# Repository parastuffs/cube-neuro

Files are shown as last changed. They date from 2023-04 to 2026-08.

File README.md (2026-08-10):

# Early Curiosity - Cube

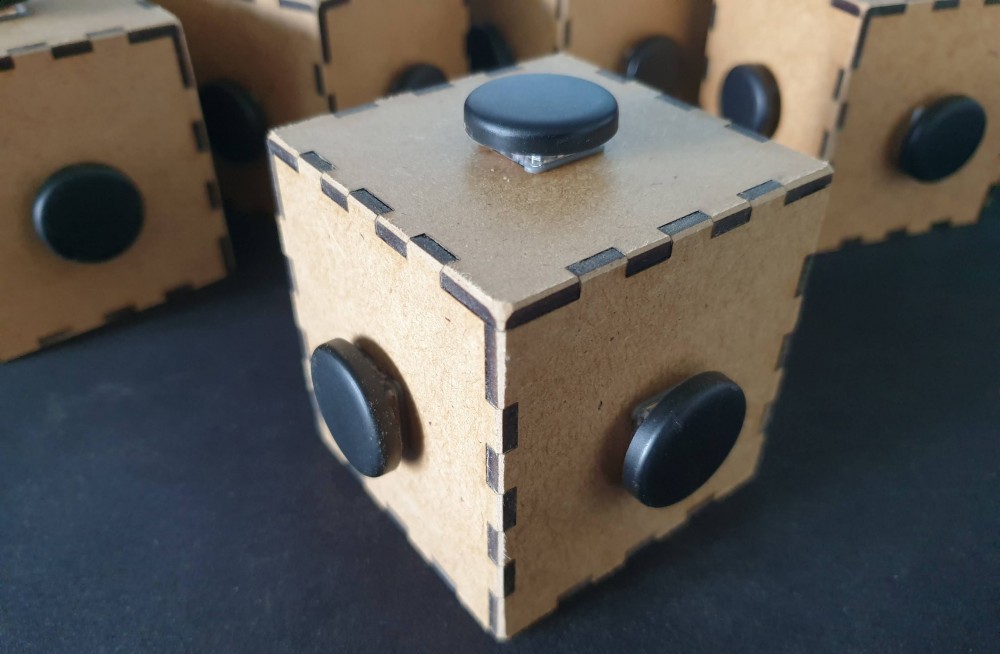
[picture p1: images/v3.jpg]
Cubes


This is the documentation for the **third version** of the cube. v1 is available [here](https://github.com/parastuffs/cube-neuro/blob/main/README_V1.md) and v2 [here](https://github.com/parastuffs/cube-neuro/blob/main/README_V2.md).
Pictures of the development are available [online](https://photos.app.goo.gl/61a8nF2CPd1NJpt47)(v2 [here](https://photos.app.goo.gl/r4oXzCXrc1rNYwXG9)).

The cube has a button on five of its faces, and a hatch on the bottom face.
Under the hatch, there is:
- A USB-C port for programming and battery charging. 
> [!IMPORTANT]  
> To charge the battery, the cube needs to be **on**.
- A switch to turn the cube on and off.
- A micro-SD reader.

In the demonstration mode, pressing a button might trigger a sound depending on the cube configuration.
> [!IMPORTANT]
> To switch to experiment mode, you need to keep any of the buttons pressed for two seconds.
In order to come back to demonstration mode, you need to reboot the cube by turning it off and on again.

In experiment mode, pressing a button never triggers a sound, but all events are saved to the SD card in a `.csv` file. It follows this structure:

| observation | face | pression_start | pression_stop | sound | isExperiment |
| --- | --- | --- | --- | --- | --- |
| Observation count, incremental | 1 to 5 value of the pressed button | Time of start of press | Time of end of press | Sound played (1) or not (0) | Press durring demo (0) or experiment (1) |

Time measurement is in milliseconds, 0 being the powering up of the cube.

### Change the sound played during demonstration mode
The sound must be located at the root of the micro-SD card and **must** be named `sound.mp3`.

### The cube and dates
The micro-controller does not have any notion of the actual date. With each reboot, it starts couting time from zero again. All files are thus created with an erroneous creation date which should be ignored.

### File structure
Upon starting for the first time, the micro-controller checks if the file `exp_id.txt` exists and does create it if it's not found.
This file contains a list of all incremental IDs of previously saved experiments.
When the cube switches to experiment mode, the micro-controller checks the last ID in that file, increment it, and create a new experiment ID.
This number `<id>` is then used to create a file `exp_<id>.csv`.

Just like audio file, experiment file names are not case sensitive (`EXP_20.csv` is the same as `exp_20.csv`) and cannot exceed eight characters without the file extension (`exp_20.csv` is valid, `experience_20.csv` or `exp_12345.csv` are not).

### Update the cube configuration
In their default configuration, the cube behave as such in demonstration mode:
- Alpha: Always play sound
- Beta: No sound
- Gamma: Sound / No sound
- Delta: No sound x7 / Sound

A more detailed guide is available [here](https://github.com/parastuffs/cube-neuro/tree/main/code) on updating the code.

### Hardware
This [file](https://github.com/parastuffs/cube-neuro/blob/main/BOM.md) has a full bill of materials. Since v3, the cube is laser cutted instead of 3D printed.

### Improvement considered
- Add an RTC to keep track of time.
- Having a configuration file for the cube type.

Copyright © 2026 Quentin Delhaye, Romain di Stasi, Claire Kabdebon, Adélaïde de Heering.

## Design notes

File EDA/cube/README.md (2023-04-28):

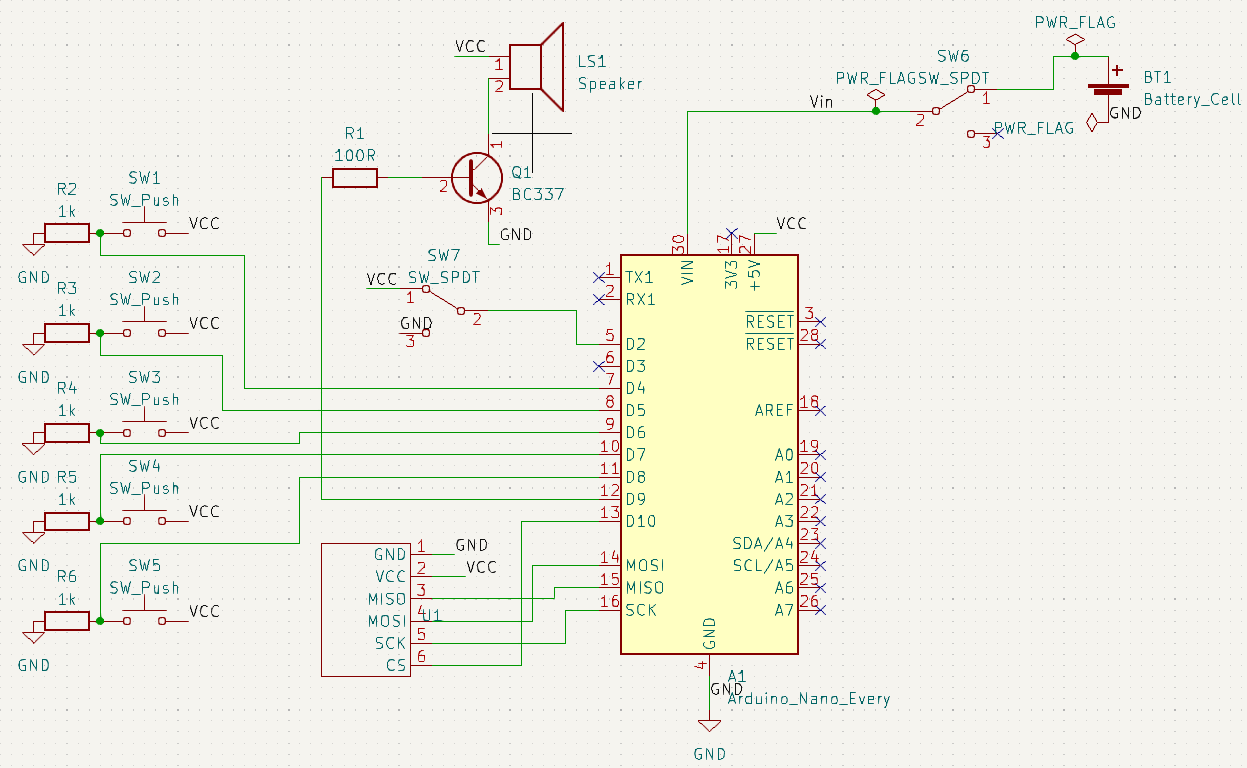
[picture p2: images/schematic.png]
Schematic


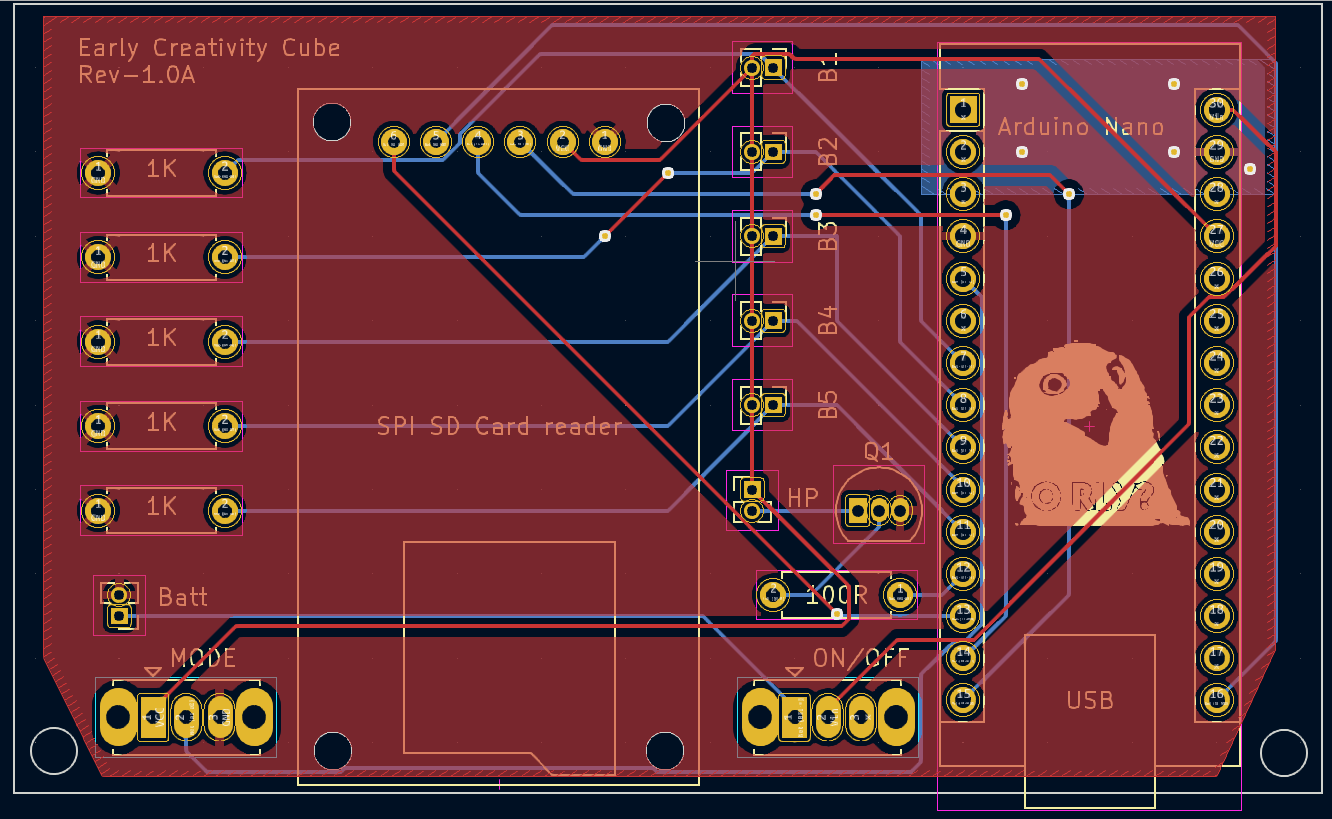
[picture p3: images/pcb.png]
PCB


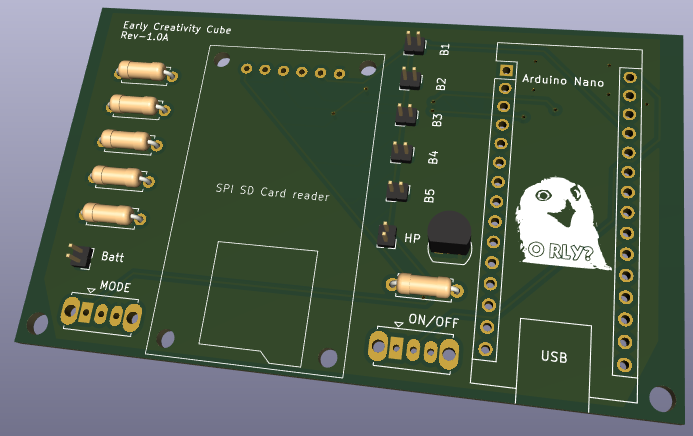
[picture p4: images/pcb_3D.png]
PCB 3D view


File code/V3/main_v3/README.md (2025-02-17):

Étant donné qu'il s'agit du même matériel, la procédure de mise à jour et de monitoring du cube est [la même que pour la V2](https://github.com/parastuffs/cube-neuro/blob/main/code/V2/README.md).

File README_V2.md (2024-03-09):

# Early Creativity - Cube

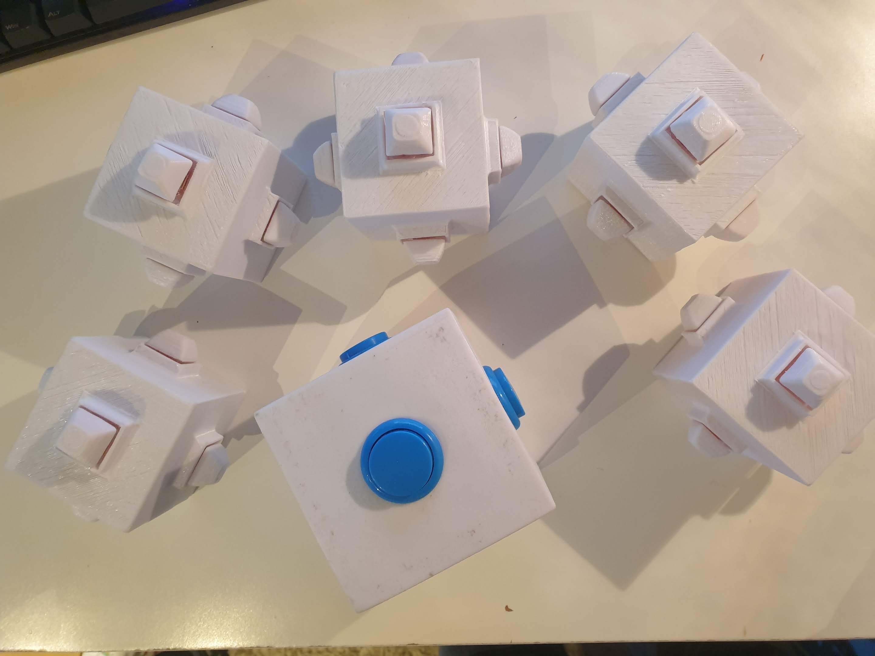
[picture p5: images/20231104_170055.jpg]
Cubes


Ceci est la documentation pour la seconde version du cube. La première version (V1) est disponible [ici](https://github.com/parastuffs/cube-neuro/blob/main/README_V1.md)
D'autres photos du développement du cube sont disponibles [en ligne](https://photos.app.goo.gl/r4oXzCXrc1rNYwXG9).

Le cube présente un bouton sur cinq de ses faces et une trappe sous sa face inférieure.
Sous la trappe se trouvent :
- Un port micro-USB pour reprogrammer le micro-contrôleur et recharger la batterie. **Attention, pour recharger la batterie, il faut connecter le câble USB et allumer le cube.**
- Un interrupteur permettant d'allumer (ON) ou éteindre (OFF) le cube.
- Un lecteur de carte micro-SD.

En mode démonstration, appuyer sur un bouton peut générer un son à l'aide du haut-parleur exposé sur la face inférieure.
**Pour passer au mode expérience, il faut maintenir un bouton enfoncé au moins deux secondes.**
Pour revenir au mode démonstration, il faut redémarrer le cube.

En mode expérience, appuyer sur un bouton ne génère aucun son, mais les pressions sont enregistrée sur la carte micro-SD dans un fichier `.csv`. Ce fichier suit la structure suivante :

| observation | face | pression_start | pression_stop | sound | isExperiment |
| --- | --- | --- | --- | --- | --- |
| Numéro de l'observation, incrémental | Valeur entre 1 et 5 du bouton appuyé | Instant de début de pression | Instant de fin de pression | Son joué (1) ou non (0) | Pression durant la démo (0) ou l'expérience (1) |

La mesure du temps se fait en milliseconde, l'instant initial étant l'allumage du cube.

Les boutons sont numérotés comme suit :
1. Face supérieure
2. Face latérale côté haut-parleur
3. Face latérale côté circuit imprimé (opposée au haut-parleur)
4. Face latérale gauche (face inférieure vers soi)
5. Face latérale droite (face inférieure vers soi)

### Changer le son joué en mode démonstration
Le son joué doit se trouver à la racine de la carte micro-SD et **doit** se nommer `sound.mp3`.

### Le cube et la notion de temps
Le micro-contrôleur n'a pas de notion de date. À chaque démarrage, il recommence à compte le temps qui passe à partir de zéro. Les fichiers créés ont donc tous la même date de création erronée qui ne doit pas être prise en compte.

### Structure des fichiers
Lors de son premier démarrage, le micro-contrôleur vérifie si le fichier `exp_id.txt` existe et le crée s'il n'est pas présent sur la carte micro-SD.
Ce dernier contient une liste des identifiants incrémentaux d'expériences enregistrées.
Au passage du cube en mode expérience (mode B), le micro-contrôleur regarde le dernier identifiant dans ce fichier et incrémente sa valeur afin de créer un nouvel identifiant d'expérience.
Cet identifiant `<id>` est ensuite utilisé pour créer un fichier `exp_<id>.csv`.

Tout comme les fichiers audio, les noms des fichiers d'expérience ne sont pas sensible à la casse (`EXP_20.CSV` est identique à `exp_20.csv`) et ne peuvent pas dépasser huit caractères, extension non-comprise (`exp_20.csv` est valable, mais `experience_20.csv` ou `exp_12345.csv` ne sont pas valable).

### Mettre à jour la configuration des cubes
Dans leur configuration par défaut, les cubes se comportent comme suit en mode démonstration :
- Alpha : son à chaque pression
- Beta : aucun son
- Gamma : son une pression sur deux
- 
- Les boutons rouges suivent le schéma suivant lors de pressions successives : pas de son / son / pas de son *ou* son / pas de son / son en fonction de la configuration souhaitée.
- Les boutons verts ne génère aucun sons.

Un guide plus détaillé est disponible [ici](https://github.com/parastuffs/cube-neuro/tree/main/code) sur la mise à jour du code sur le micro-contrôleur.

### Matériel utilisé
Le fichier [suivant](https://github.com/parastuffs/cube-neuro/blob/main/BOM.md) contient un tableau avec l'ensemble du matériel utilisé pour réaliser un cube complet.

### Améliorations possibles
- Ajouter une RTC pour que le cube connaisse la date des expériences.
- Prévoir un meilleur circuit d'amplification pour le haut-parleur afin d'obtenir un meilleur volume sonore.
- Choisir le mode de fonctionnement du cube en mode démonstration (A) via un fichier de configuration sur la carte SD.

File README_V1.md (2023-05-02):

# Early Creativity - Cube

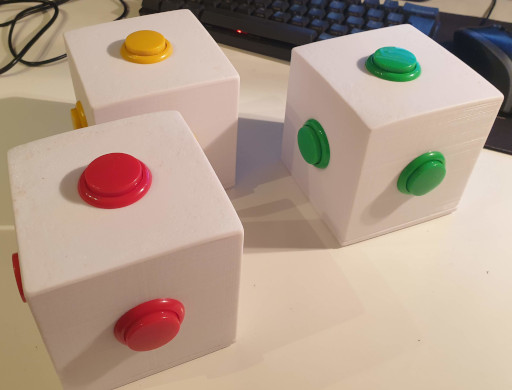
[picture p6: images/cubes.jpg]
Cubes


Le cube présente un bouton sur cinq de ses faces et une trappe sous sa face inférieure.
Sous la trappe se trouvent :
- Un port mini-USB pour reprogrammer le micro-contrôleur.
- Un port micro-USB pour recharger la batterie.
- Un interrupteur permettant d'allumer (ON) ou éteindre (OFF) le cube.
- Un interrupteur permettant de choisir le mode de fonctionnement: démonstration (A) ou expérience (B).
- Un lecteur de carte micro-SD.

En mode démonstration (A), appuyer sur un bouton peut générer un son à l'aide du haut-parleur exposé sur la face inférieure.

En mode expérience (B), appuyer sur un bouton ne génère aucun son, mais les pressions sont enregistrée sur la carte micro-SD dans un fichier `.csv`. Ce fichier suit la structure suivante :

| observation | face | pression_start | pression_stop | sound |
| --- | --- | --- | --- | --- |
| Numéro de l'observation, incrémental | Valeur entre 1 et 5 du bouton appuyé | Instant de début de pression | Instant de fin de pression | Son joué (1) ou non (0) |

La mesure du temps se fait en milliseconde, l'instant initial étant l'allumage du cube.

Les boutons sont numérotés comme suit :
1. Face supérieure
2. Face latérale côté haut-parleur
3. Face latérale côté circuit imprimé (opposée au haut-parleur)
4. Face latérale gauche (face inférieure vers soi)
5. Face latérale droite (face inférieure vers soi)

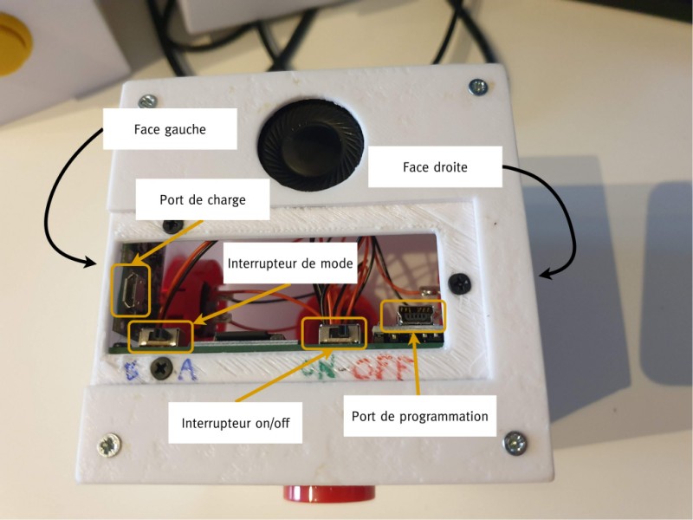
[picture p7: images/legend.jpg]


### Changer le son joué en mode démonstration
Le son joué doit se trouver à la racine de la carte micro-SD et **doit** se nommer `sound.wav`.
Le nom du fichier ne peut pas dépasser **8** caractères (hors extension). Par exemple, `maman.wav` est valable (« maman » faisant moins de huit caractères), mais `hydravion.wav` n'est pas valable.
Le système est insensible à la casse, `maman.wav` et `MaMaN.wav` sont interprétés comme étant le même fichier.

Le fichier audio **doit** respecter les contraintes suivantes :
- Codec WAV PCM 8-bit
- Mono
- Taux d'échantillonnage entre 8 kHz et 32 kHz.

La [documentation de la bibliothèque](https://github.com/TMRh20/TMRpcm/wiki) donne des informations supplémentaires si nécessaire.

### Le cube et la notion de temps
Le micro-contrôleur n'a pas de notion de date. À chaque démarrage, il recommence à compte le temps qui passe à partir de zéro. Les fichiers créés ont donc tous la même date de création erronée qui ne doit pas être prise en compte.

### Structure des fichiers
Lors de son premier démarrage, le micro-contrôleur vérifie si le fichier `exp_id.txt` existe et le crée s'il n'est pas présent sur la carte micro-SD.
Ce dernier contient une liste des identifiants incrémentaux d'expériences enregistrées.
Au passage du cube en mode expérience (mode B), le micro-contrôleur regarde le dernier identifiant dans ce fichier et incrémente sa valeur afin de créer un nouvel identifiant d'expérience.
Cet identifiant `<id>` est ensuite utilisé pour créer un fichier `exp_<id>.csv`.

Tout comme les fichiers audio, les noms des fichiers d'expérience ne sont pas sensible à la casse (`EXP_20.CSV` est identique à `exp_20.csv`) et ne peuvent pas dépasser huit caractères, extension non-comprise (`exp_20.csv` est valable, mais `experience_20.csv` ou `exp_12345.csv` ne sont pas valable).

### Mettre à jour la configuration des cubes
Dans leur configuration par défaut, les cubes se comportent comme suit en mode démonstration :
- Les boutons jaunes génèrent systématiquement un son.
- Les boutons rouges suivent le schéma suivant lors de pressions successives : pas de son / son / pas de son *ou* son / pas de son / son en fonction de la configuration souhaitée.
- Les boutons verts ne génère aucun sons.

Un guide plus détaillé est disponible [ici](https://github.com/parastuffs/cube-neuro/tree/main/code) sur la mise à jour du code sur le micro-contrôleur.

### Matériel utilisé
Le fichier [suivant](https://github.com/parastuffs/cube-neuro/blob/main/BOM.md) contient un tableau avec l'ensemble du matériel utilisé pour réaliser un cube complet.

### Améliorations possibles
- Ajouter une RTC pour que le cube connaisse la date des expériences.
- Décaler le support du circuit imprimé pour permettre à la trappe de se placer correctement sous le cube.
- Prévoir un meilleur circuit d'amplification pour le haut-parleur afin d'obtenir un meilleur volume sonore.
- Choisir le mode de fonctionnement du cube en mode démonstration (A) via un fichier de configuration sur la carte SD.

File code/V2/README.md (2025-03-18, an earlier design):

## Comment mettre le code à jour sur le micro-contrôleur ?
Le micro-contrôleur utilisé est un **Wemos Lolin32 Lite**. La méthode la plus facile pour le programmer est d'utiliser l'environnement de développement intégré (IDE) Arduino.
Ce dernier est téléchargeable [sur le site du fabricant](https://support.arduino.cc/hc/en-us/articles/360019833020-Download-and-install-Arduino-IDE).

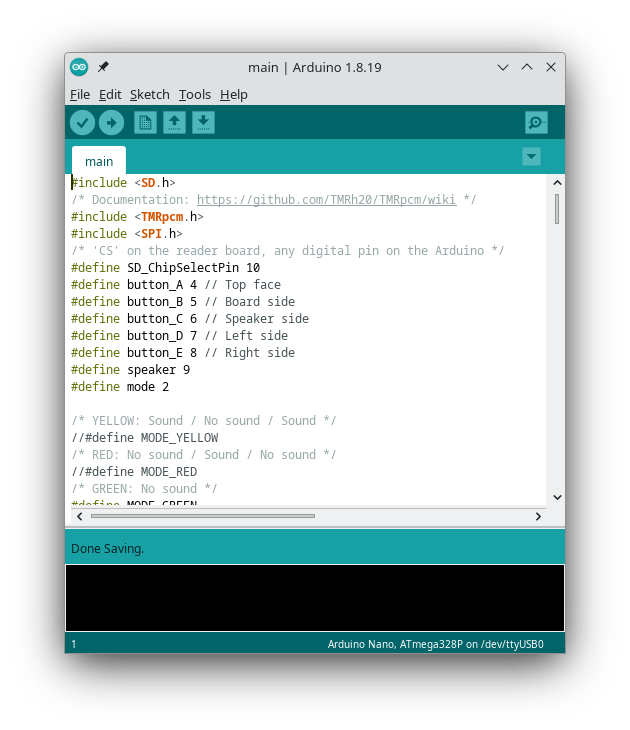
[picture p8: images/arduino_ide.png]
Arduino IDE


Avant tout, assurez-vous que les bibliothèques nécessaires sont correctement installées.

1. Allez dans le menu `Tools > Boards > Boards Manager...` et vérifiez que `ESP32` version `2.0.17` est installé.
Boards manager
2. Allez dans le menu `Tools > Manage Libraries...` et installez la bibliothèques `SD` version 1.2.4 (gestion de la carte SD), TMRpcm version 1.2.3 (gestion des fichier audio au format WAV), ainsi que `ESP32LitePack`.
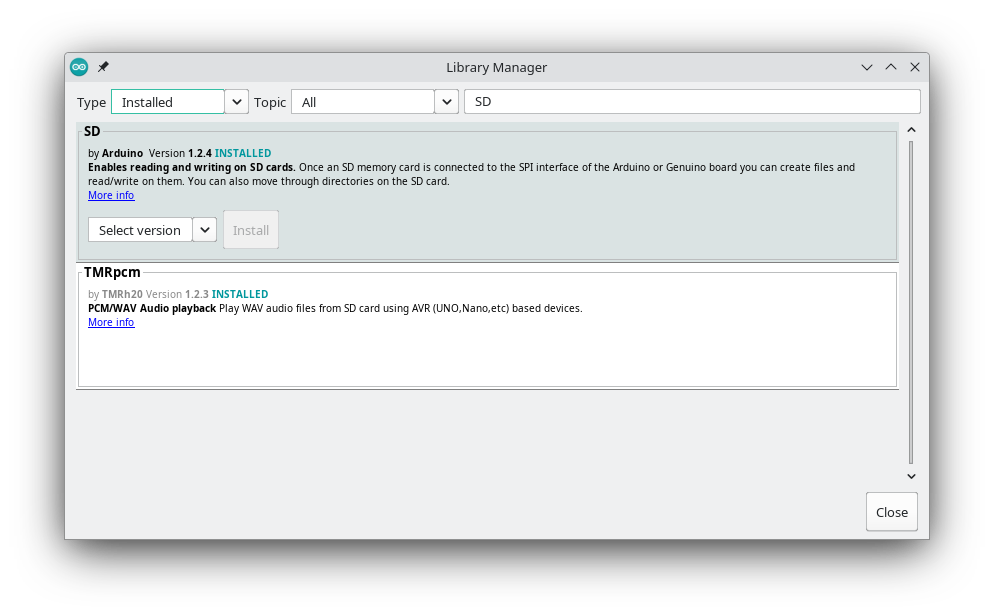
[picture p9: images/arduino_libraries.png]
Libraries Manager

3. Téléchargez la bibliothèque audio [ici](https://github.com/schreibfaul1/ESP32-audioI2S/archive/refs/tags/3.0.8.zip) et suivez [ce guide](https://github.com/schreibfaul1/ESP32-audioI2S/wiki#can-the-arduino-ide-be-used) pour l'installer.

Sélectionnez ensuite la bonne carte dans la liste des cartes supportées dans le menu `Tools > Boards > ESP32 Arduino > WEMOS LOLIN32 Lite`.

Allez ensuite dans le menu `Tools > Port` et sélectionnez le bon port auquel est connecté la carte. La plupart du temps, il sera sélectionné par défaut.

Veillez à bien sélectionner l'option suivante : `Tools > Partition Scheme > No OTA (Large APP)`

Vous pouvez **compiler** votre code en cliquant sur le « ✓ » (checkmark) en haut à gauche de l'interface.
Vous pouvez **uploader** (téléverser) votre code sur l'Arduino en cliquant sur la « → » (flèche pointant à droite) en haut à gauche de l'interface.

## Troubleshooting
Si le code refuse de s'envoyer vers le micro-contrôleur, vérifiez les éléments suivants :
- Il est bien connecté à votre ordinateur.
- Le bon type de carte est sélectionné : `WEMOS LOLIN32 Lite`.
- Sélectionnez le bon port.

Si le programme ne fonctionne pas, essayez de l'exécuter tout en étant connecté à l'IDE et appuyez sur la petite loupe en haut à droite de l'interface. Vérifiez que l'option « 115200 baud » est bien sélectionnée dans la fenêtre.
Sur le micro-contrôleur, appuyez sur le bouton à côté du port USB pour le redémarrer et vérifiez qu'il ne vous dit pas `SD Failed`, ce qui vous indiquerait que la carte SD n'est pas correctement insérée ou que le fichier audio `sound.mp3` est absent de la carte.
Si l'enregistrement des données s'arrête après une pression, reprogrammez le cube.

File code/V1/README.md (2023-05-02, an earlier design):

Attention, veillez à ne connecter le micro-contrôleur à votre ordinateur **que si le cube est éteint !** Le micro-contrôleur n'apprécie pas de recevoir 5 V de la batterie *et* du câble USB en m

## Comment mettre le code à jour sur le micro-contrôleur ?
Le micro-contrôleur utilisé est un **Arduino Nano** (ou équivalent). La méthode la plus facile pour le programmer est d'utiliser l'environnement de développement intégré (IDE) officiel.
Ce dernier est téléchargeable [sur le site du fabricant](https://support.arduino.cc/hc/en-us/articles/360019833020-Download-and-install-Arduino-IDE).

Arduino IDE

Avant tout, assurez-vous que les bibliothèques nécessaires sont correctement installées.

1. Allez dans le menu `Tools > Boards > Boards Manager...` et vérifiez que « Arduino AVR Boards » est installé.
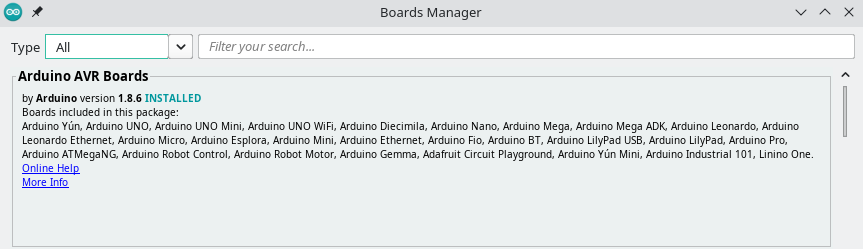
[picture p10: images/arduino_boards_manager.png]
Boards manager

2. Allez dans le menu `Tools > Manage Libraries...` et installez la bibliothèques `SD` (gestion de la carte SD) ainsi que `TMRpcm` (gestion de l'audio).
Libraries Manager

Sélectionnez ensuite la bonne carte dans la liste des cartes supportées dans le menu `Tools > Boards > Arduino AVR Boards > Arduino Nano`.

Allez ensuite dans le menu `Tools > Port` et sélectionnez le bon port auquel est connecté la carte. La plupart du temps, il sera sélectionné par défaut.

Vous pouvez **compiler** votre code en cliquant sur le « ✓ » (checkmark) en haut à gauche de l'interface.
Vous pouvez **uploader** (téléverser) votre code sur l'Arduino en cliquant sur la « → » (flèche pointant à droite) en haut à gauche de l'interface.

## Troubleshooting
Si le code refuse de s'envoyer vers le micro-contrôleur, vérifiez les éléments suivants :
- Il est bien connecté à votre ordinateur.
- Le bon type de carte est sélectionné : Arduino Nano.
- Sélectionnez le bon port.
- Essayez de changer le programmeur : `Tools > Processor > ATmega328P (Old Bootloader)`.

Si le programme ne fonctionne pas, essayez de l'exécuté tout en étant connecté à l'IDE et appuyez sur la petite loupe en haut à droite de l'interface.
Appuyez sur le bouton au centre de l'Arduino pour le redémarrer et vérifiez qu'il ne vous dit pas `SD Failed`, ce qui vous indiquerait que la carte SD n'est pas correctement insérée ou que le fichier audio `sound.wav` est absent de la carte.

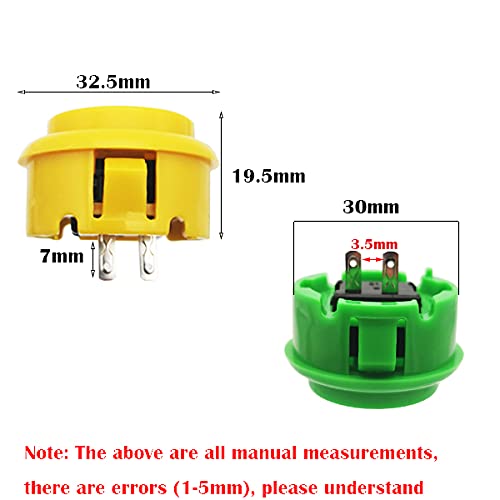
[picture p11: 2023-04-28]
images/arcade.jpg

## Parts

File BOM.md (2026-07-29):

## V3
| Item | Quantity | Usage | Product link | Documentation |
| --- | --- | --- | --- | --- |
| M2.5x10mm Screw | 4 | PCB and SD card reader on support boards | [Link](https://www.aliexpress.com/item/1005005984419378.html) | N/A |
| M2.5 nuts | 4 | Securing screws | N/A | N/A |
| 4mmx2mm magnets | 2 | Hatch | [Link](https://www.aliexpress.com/item/1005006362930902.html) | N/A |
| Lolin32 Lite USB-C | 1 | Micro-controller | [Link](https://www.aliexpress.com/item/1005006267442536.html) | N/A |
| 1GB Micro-SD card | 1 | Storage | [Link](https://www.aliexpress.com/item/1005005730937046.html) | N/A |
| Kailh Deep Sea Silent Mini Mechanical Switches | 5 | Main buttons | [Link](https://nl.aliexpress.com/item/1005008382793794.html) | N/A |
| Arcade button caps   | 5 | Main buttons caps | [Link](https://nl.aliexpress.com/item/1005005970271632.html) | N/A |
| 3.7V 1100mAh battery 603449 | 1 | Battery | [Link](https://www.amazon.com.be/dp/B08VRYS8FT) | N/A |
| 2W/8Ω speaker, 23 mm | 1 | Speaker | [Link](https://nl.aliexpress.com/item/4000147941440.html) | N/A |
| JST cables 1.25mm male | 2 | Connecting battery and speaker on the PCB | [Link](https://www.amazon.fr/dp/B08JV96C4N) | N/A |
| JST connectors 1.25mm femelle | 2 | Connecting battery and speaker on the PCB | [Link](https://www.amazon.fr/dp/B0B3NGZG5N) | N/A |
| SPI micro-SD card reader | 1 | Storage reader | [Link](https://www.aliexpress.com/item/1005005591145849.html) | N/A |
| Switch SK12D07VG3 | 1 | On/off mode | [Link](https://www.amazon.fr/dp/B08SM2HHNR) | [Link](https://datasheet.lcsc.com/lcsc/1912111437_SHOU-HAN-SK12D07VG3_C431547.pdf) |
| Printed circuit board | 1 | Connecting electronic components | [Link](https://aisler.net/) | [Link](https://github.com/parastuffs/cube-neuro/tree/main/EDA/wood-cube) 
| Resistor 1kΩ | 5 | Pull-down for buttons | N/A | N/A |
| Resistor 100kΩ | 2 | Input resistors for audio amplifier | N/A | N/A |
| Capacitor 100nF | 2 | Input capacitors for audio amplifier | N/A | N/A |
| Capacitor 1µF | 1 | Power bypass capacitor for audio amplifier | N/A | N/A |
| PAM8304ASR | 1 | Audio amplifier circuit | [Link](https://www.aliexpress.com/item/1005005308251005.html) | [Link](https://www.diodes.com/assets/Datasheets/PAM8304.pdf) |

## V2
| Objet | Quantité | Utilisation | Lien produit | Documentation |
| --- | --- | --- | --- | --- |
| Vis M2.5x5mm | 2 | Trappe inférieure | N/A | N/A |
| Écrous M2.5 | 2 | Trappe inférieure | N/A | N/A |
| Aimants S-04-02-N | 2 | Trappe inférieure | [Lien](https://www.supermagnete.be/fre/aimants-disques-neodyme/disque-magnetique-4mm-2mm_S-04-02-N) | N/A |
| Vis M2.5x30mm | 4 | Fixer la partie inférieure | N/A | N/A |
| Vis M2x7mm | 2 | Fixer le circuit imprimé à la partie inférieure | N/A | N/A |
| PLA blanc 1.75mm | 38.264 m (115 g) | Impressions 3D | [Lien](https://www.amazon.fr/Geeetech-Filament-1-75-imprimante-couleur/dp/B01MR5OCX5/) | N/A |
| Lolin32 Lite | 1 | Micro-contrôleur | [Lien](https://www.az-delivery.de/fr/products/esp32-lolin-lolin32) | N/A |
| Carte micro-SD 8 Go | 1 | Stockage | [Lien](https://www.amazon.fr/dp/B0876H3YBQ) | N/A |
| Switches linéaires 38gf | 5 | Boutons principaux | [Lien](https://www.amazon.fr/gp/product/B0C6K7CX31/) | N/A |
| Batterie 3.7V 320mAh 402535 | 1 | Batterie | [Lien](https://www.amazon.fr/gp/product/B08HD1N273) | N/A |
| Haut-parleur 2W/8 Ω, 2.8 cm | 1 | Haut-parleur | [Lien](https://www.amazon.fr/dp/B09MRK24PP) | N/A |
| Câbles JST 1.25mm mâles | 7 | Connexion des éléments sur le circuit imprimé | [Lien](https://www.amazon.fr/dp/B08JV96C4N) | N/A |
| Câbles JST 1.25mm femelle | 1 | Connexion batterie au contrôleur de charge | [Lien](https://www.amazon.fr/dp/B08JV96C4N) | N/A |
| Câbles micro-USB | 1 | Charge batterie | [Lien](https://www.amazon.fr/dp/B07GQZHV12) | N/A |
| Lecteur carte micro-SD SPI | 1 | Lecteur pour support de stockage | [Lien](https://www.amazon.fr/dp/B077MB17JB) | [Lien](https://cdn.shopify.com/s/files/1/1509/1638/files/SPI_Reader_Micro_Speicherkartenmodul_Pinout.pdf?6382365621849770781) |
| Interrupteur SK12D07VG3 | 1 | Choix du mode et on/off | [Lien](https://www.amazon.fr/dp/B08SM2HHNR) | [Lien](https://datasheet.lcsc.com/lcsc/1912111437_SHOU-HAN-SK12D07VG3_C431547.pdf) |
| Connecteurs JST 1.25mm femelle | 9 | Connexion des éléments sur le circuit imprimé | [Lien](https://www.amazon.fr/dp/B0B3NGZG5N) | N/A |
| Circuit imprimé | 1 | Interconnexion des éléments | [Lien](https://jlcpcb.com/) | [Lien](https://github.com/parastuffs/cube-neuro/tree/main/EDA/cube) 
| Résistance 1 kΩ | 5 | Pull-down des boutons | N/A | N/A |
| Résistance 100 Ω | 1 | Résistance de base du NPN | N/A | N/A |
| BC337-25 | 1 | Transistor NPN pour amplifier l'audio | N/A | [Lien](https://www.sparkfun.com/datasheets/Components/BC546.pdf) |

## V1
| Objet | Quantité | Utilisation | Lien produit | Documentation |
| --- | --- | --- | --- | --- |
| Vis M2.5x5mm | 3 | Trappe inférieure | N/A | N/A |
| Écrous M2.5 | 3 | Trappe inférieure | N/A | N/A |
| Aimants S-04-02-N | 3 | Trappe inférieure | [Lien](https://www.supermagnete.be/fre/aimants-disques-neodyme/disque-magnetique-4mm-2mm_S-04-02-N) | N/A |
| Vis M2.5x30mm | 4 | Fixer la partie inférieure | N/A | N/A |
| Vis M2x7mm | 2 | Fixer le circuit imprimé à la partie inférieure | N/A | N/A |
| PLA blanc 1.75mm | 38.264 m (115 g) | Impressions 3D | [Lien](https://www.amazon.fr/Geeetech-Filament-1-75-imprimante-couleur/dp/B01MR5OCX5/) | N/A |
| Boutons d'arcade | 5 | Boutons principaux | [Lien](https://www.amazon.fr/dp/B098J38KPJ) | [Lien](https://github.com/parastuffs/cube-neuro/raw/main/images/arcade.jpg) |
| Carte micro-SD 8 Go | 1 | Stockage | [Lien](https://www.amazon.fr/dp/B0876H3YBQ) | N/A |
| Arduino Nano | 1 | Micro-contrôleur | [Lien](https://www.amazon.fr/dp/B0722YYBSS) | [Lien](https://docs.arduino.cc/hardware/nano) |
| Câble mini-USB | 1 | Connexion micro-contrôleur | [Lien](https://www.amazon.fr/dp/B07NSQ511V) | N/A |
| Batterie 3.7V 1100mAh 1S 1C | 1 | Batterie | [Lien](https://www.amazon.fr/dp/B087LTZW61) | N/A |
| Haut-parleur 2W/8 Ω, 2.8 cm | 1 | Haut-parleur | [Lien](https://www.amazon.fr/dp/B09MRK24PP) | N/A |
| Câbles JST 1.25mm mâles | 7 | Connexion des éléments sur le circuit imprimé | [Lien](https://www.amazon.fr/dp/B08JV96C4N) | N/A |
| Câbles JST 1.25mm femelle | 1 | Connexion batterie au contrôleur de charge | [Lien](https://www.amazon.fr/dp/B08JV96C4N) | N/A |
| Câbles micro-USB | 1 | Charge batterie | [Lien](https://www.amazon.fr/dp/B07GQZHV12) | N/A |
| Contrôleur de charge 18650 | 1 | Recharge batterie et alimentation 5 V micro-contrôleur | [Lien](https://www.amazon.fr/dp/B0859W837M) | N/A |
| Lecteur carte micro-SD SPI | 1 | Lecteur pour support de stockage | [Lien](https://www.amazon.fr/dp/B077MB17JB) | [Lien](https://cdn.shopify.com/s/files/1/1509/1638/files/SPI_Reader_Micro_Speicherkartenmodul_Pinout.pdf?6382365621849770781) |
| Interrupteur SK12D07VG3 | 2 | Choix du mode et on/off | [Lien](https://www.amazon.fr/dp/B08SM2HHNR) | [Lien](https://datasheet.lcsc.com/lcsc/1912111437_SHOU-HAN-SK12D07VG3_C431547.pdf) |
| Connecteurs JST 1.25mm femelle | 7 | Connexion des éléments sur le circuit imprimé | [Lien](https://www.amazon.fr/dp/B0B3NGZG5N) | N/A |
| Circuit imprimé | 1 | Interconnexion des éléments | [Lien](https://jlcpcb.com/) | [Lien](https://github.com/parastuffs/cube-neuro/tree/main/EDA/cube) 
| Résistance 1 kΩ | 5 | Pull-down des boutons | N/A | N/A |
| Résistance 100 Ω | 1 | Résistance de base du NPN | N/A | N/A |
| BC546C | 1 | Transistor NPN pour amplifier l'audio | N/A | [Lien](https://www.sparkfun.com/datasheets/Components/BC546.pdf) |

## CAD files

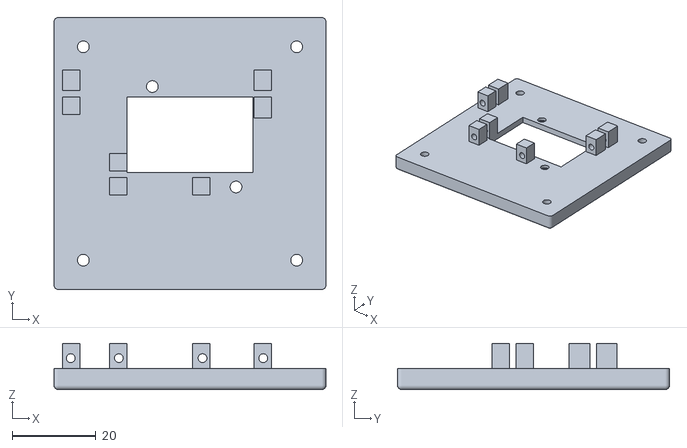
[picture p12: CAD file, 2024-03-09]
CAD/cube_v3.1-Bottom.stl
65.0 x 65.0 x 11.0

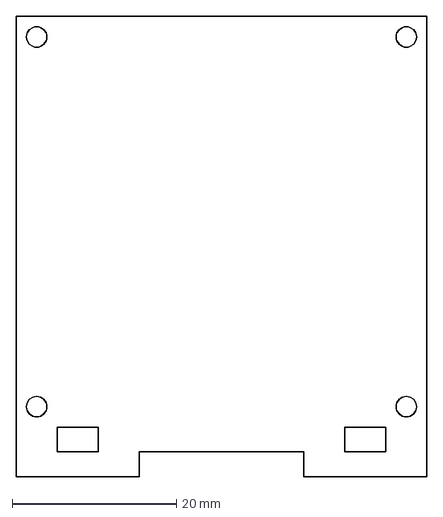
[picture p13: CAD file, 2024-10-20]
CAD/Wood cube - Laser cut/cube_v4-Shape2D_pcb_plate.dxf
50.0 x 56.0 mm

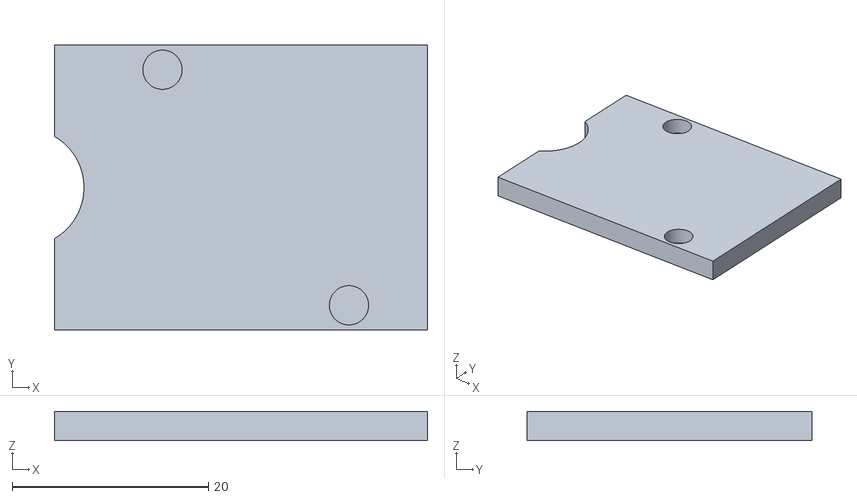
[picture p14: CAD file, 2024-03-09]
CAD/cube_v3.1-trap.stl
38.0 x 29.0 x 3.00

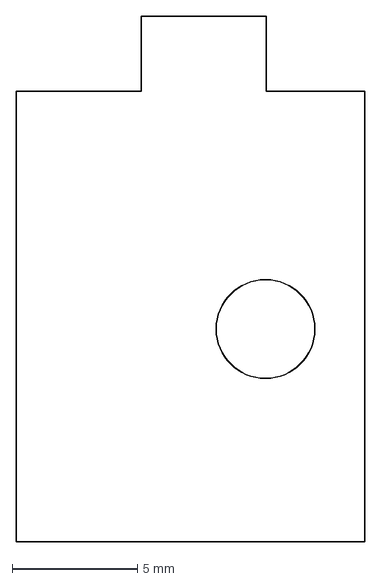
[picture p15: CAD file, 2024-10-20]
CAD/Wood cube - Laser cut/cube_v4-Shape2D_magnet_plate.dxf
14.0 x 21.0 mm

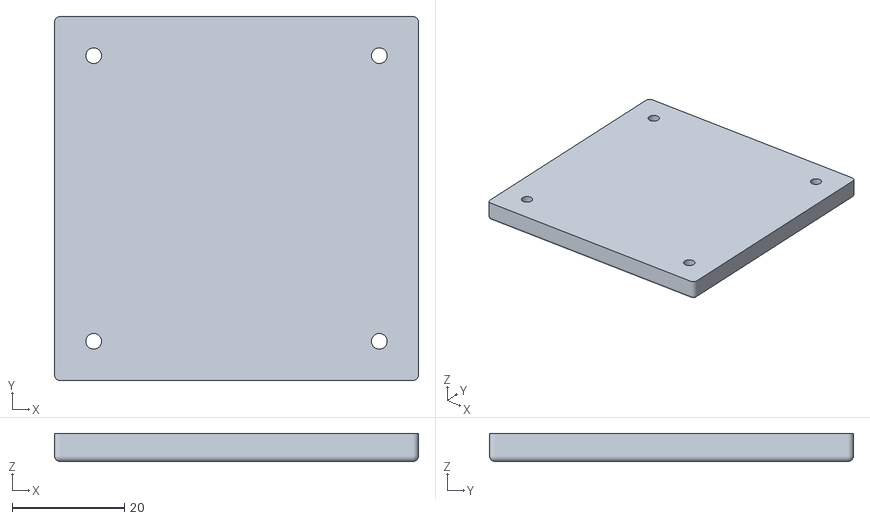
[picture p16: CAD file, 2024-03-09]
CAD/cube_v3.1-Bot_plain.stl
65.0 x 65.0 x 5.00

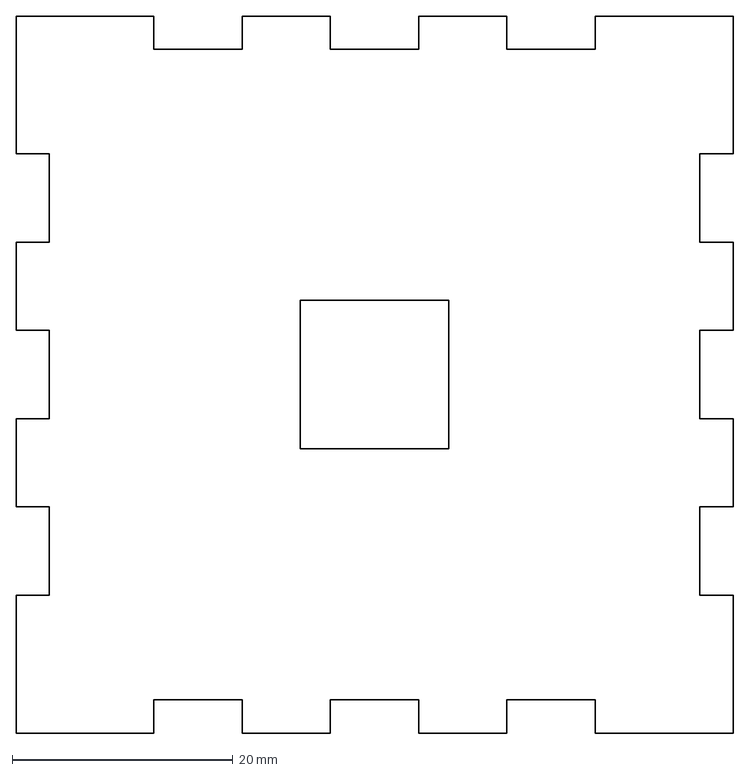
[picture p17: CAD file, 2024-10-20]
CAD/Wood cube - Laser cut/cube_v4-top001.dxf
65.0 x 65.0 mm

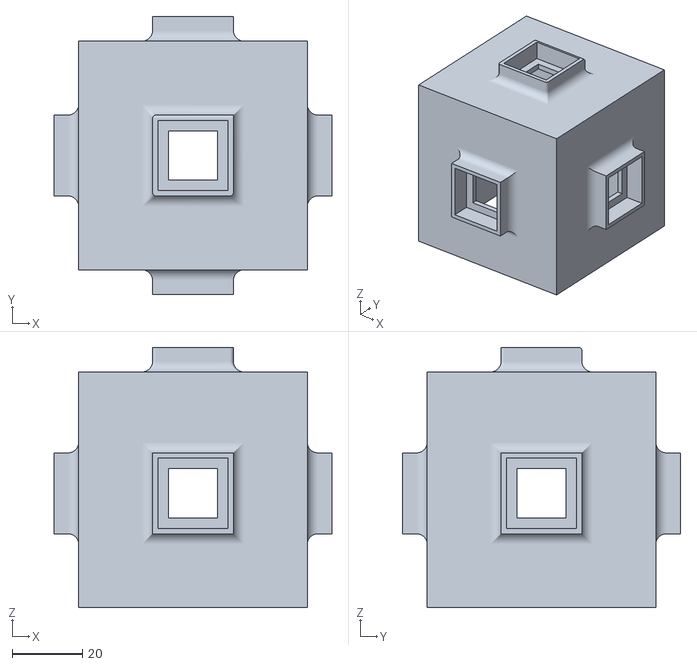
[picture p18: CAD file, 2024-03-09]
CAD/cube_v3.1-Body.stl
79.0 x 79.0 x 74.0

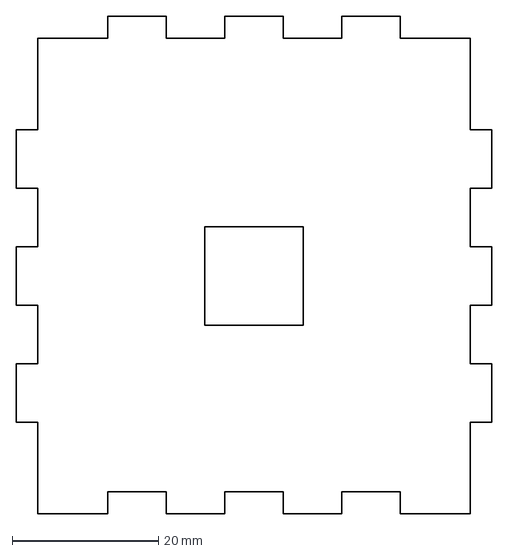
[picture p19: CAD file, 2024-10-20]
CAD/Wood cube - Laser cut/cube_v4-front.dxf
65.0 x 68.0 mm

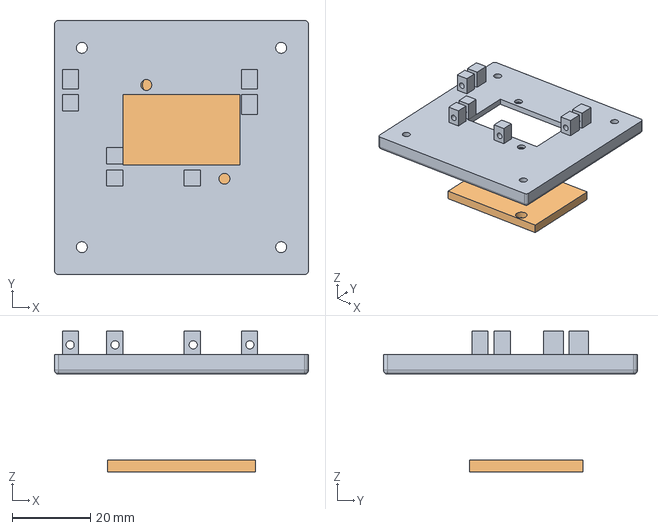
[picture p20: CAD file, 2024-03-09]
CAD/cube_v3.FCStd
65.0 x 65.0 x 36.0 mm
Bottom
trap

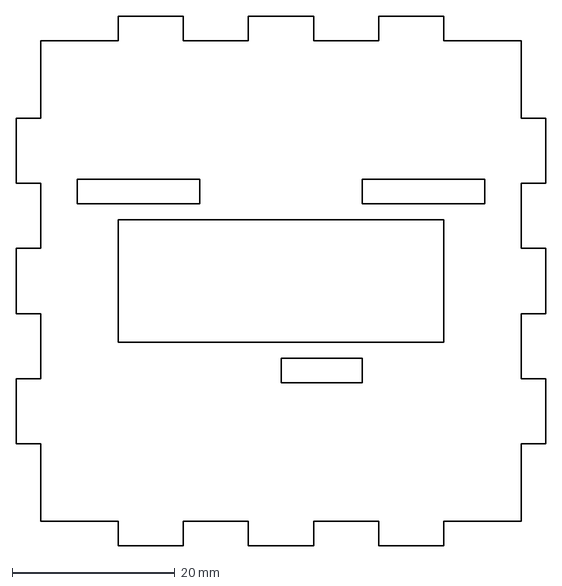
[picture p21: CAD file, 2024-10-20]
CAD/Wood cube - Laser cut/cube_v4-Shape2D_bottom.dxf
65.0 x 65.0 mm

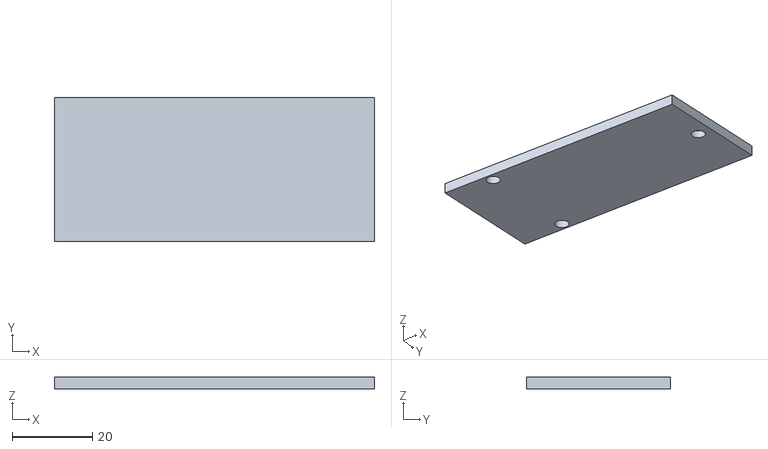
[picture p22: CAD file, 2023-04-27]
CAD/cube_v2.1-trap.stl
80.0 x 36.0 x 3.00

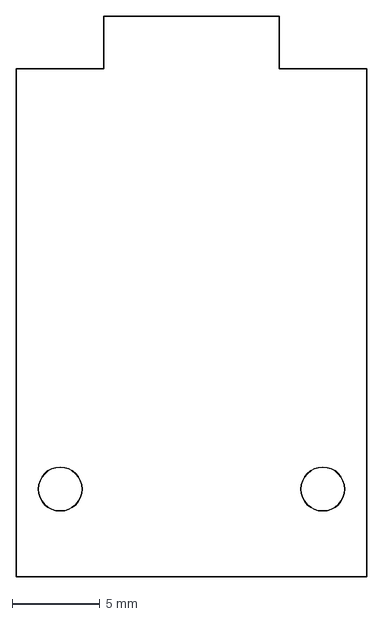
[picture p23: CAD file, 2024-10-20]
CAD/Wood cube - Laser cut/cube_v4-Shape2D_sd_plate.dxf
20.0 x 32.0 mm

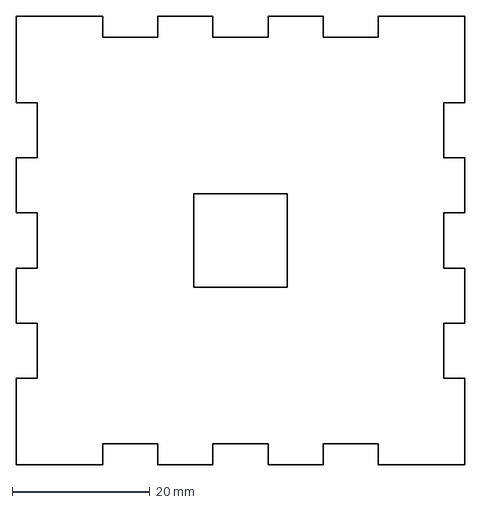
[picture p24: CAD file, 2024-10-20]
CAD/Wood cube - Laser cut/cube_v4-Shape2DView.dxf
65.0 x 65.0 mm

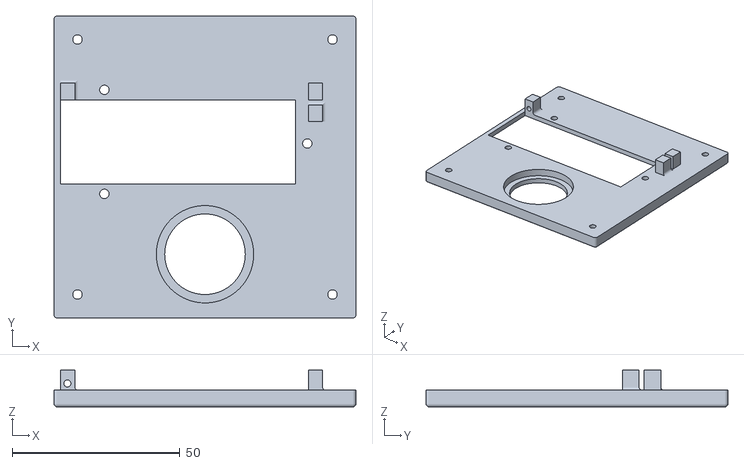
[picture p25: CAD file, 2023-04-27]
CAD/cube_v2.1-Bottom.stl
90.0 x 90.0 x 11.0

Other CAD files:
CAD/cube_v2.FCStd
CAD/Wood cube - Laser cut/cube_v4-Shape2D_spacer.dxf
CAD/Wood cube - Laser cut/cube_v4-right.dxf
CAD/Wood cube - Laser cut/cube_v4.FCStd
CAD/cube_v2.stl

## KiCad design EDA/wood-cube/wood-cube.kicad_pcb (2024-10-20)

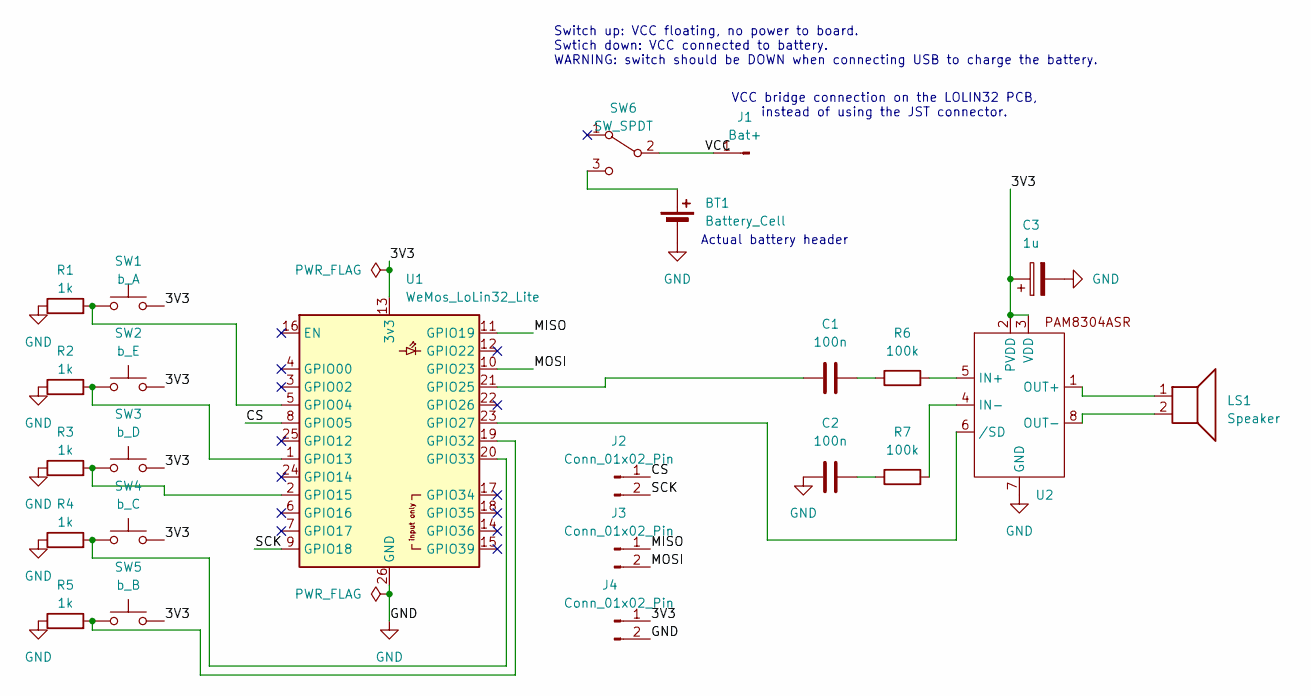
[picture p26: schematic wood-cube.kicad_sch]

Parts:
BT1: Battery_Cell; PinHeader_1x02_P1.27mm_Vertical
C1, C2: 100n; C_1206_3216Metric_Pad1.33x1.80mm_HandSolder
C3: 1u; CP_Elec_4x3.9
J1: Bat+; PinHeader_1x01_P2.54mm_Vertical
J2, J3, J4: Conn_01x02_Pin; PinHeader_1x02_P2.54mm_Vertical
LS1: Speaker; PinHeader_1x02_P1.27mm_Vertical
R1, R2, R3, R4, R5: 1k; R_1206_3216Metric_Pad1.30x1.75mm_HandSolder
R6, R7: 100k; R_1206_3216Metric_Pad1.30x1.75mm_HandSolder
SW1: b_A; PinHeader_1x02_P2.54mm_Vertical
SW2: b_E; PinHeader_1x02_P2.54mm_Vertical
SW3: b_D; PinHeader_1x02_P2.54mm_Vertical
SW4: b_C; PinHeader_1x02_P2.54mm_Vertical
SW5: b_B; PinHeader_1x02_P2.54mm_Vertical
SW6: SW_SPDT; SW_Slide_SPDT_Angled_CK_OS102011MA1Q
U1: WeMos_LoLin32_Lite; WEMOS_LoLin32_Lite
U2: MSOP-8_3x3mm_P0.65mm

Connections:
/3V3: C3.1, J4.1, SW1.2, SW2.2, SW3.2, SW4.2, SW5.2, U1.13 (3v3), U2.2 (PVDD), U2.3 (VDD)
/CS: J2.1, U1.8 (GPIO05)
/MISO: J3.1, U1.11 (GPIO19)
/MOSI: J3.2, U1.10 (GPIO23)
/SCK: J2.2, U1.9 (GPIO18)
/VCC: J1.1, SW6.2 (B)
GND: BT1.2 (-), C2.1, C3.2, J4.2, R1.1, R2.1, R3.1, R4.1, R5.1, U1.26 (GND), U2.7 (GND)
unnamed: BT1.1 (+), SW6.3 (C)
unnamed: C1.2, R6.1
unnamed: C2.2, R7.1
unnamed: R1.2, SW1.1, U1.5 (GPIO04)
unnamed: R2.2, SW2.1, U1.1 (GPIO13)
unnamed: R3.2, SW3.1, U1.2 (GPIO15)
unnamed: C1.1, U1.21 (GPIO25)
unnamed: U1.23 (GPIO27), U2.6 (/SD)
unnamed: R5.2, SW5.1, U1.19 (GPIO32)
unnamed: R4.2, SW4.1, U1.20 (GPIO33)
unnamed: R6.2, U2.5 (IN+)
unnamed: R7.2, U2.4 (IN-)
unnamed: LS1.1, U2.1 (OUT+)
unnamed: LS1.2, U2.8 (OUT-)

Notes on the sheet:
Actual battery header
Switch up: VCC floating, no power to board. Swtich down: VCC connected to battery. WARNING: switch should be DOWN when connecting USB to charge the battery.
VCC bridge connection on the LOLIN32 PCB, instead of using the JST connector.

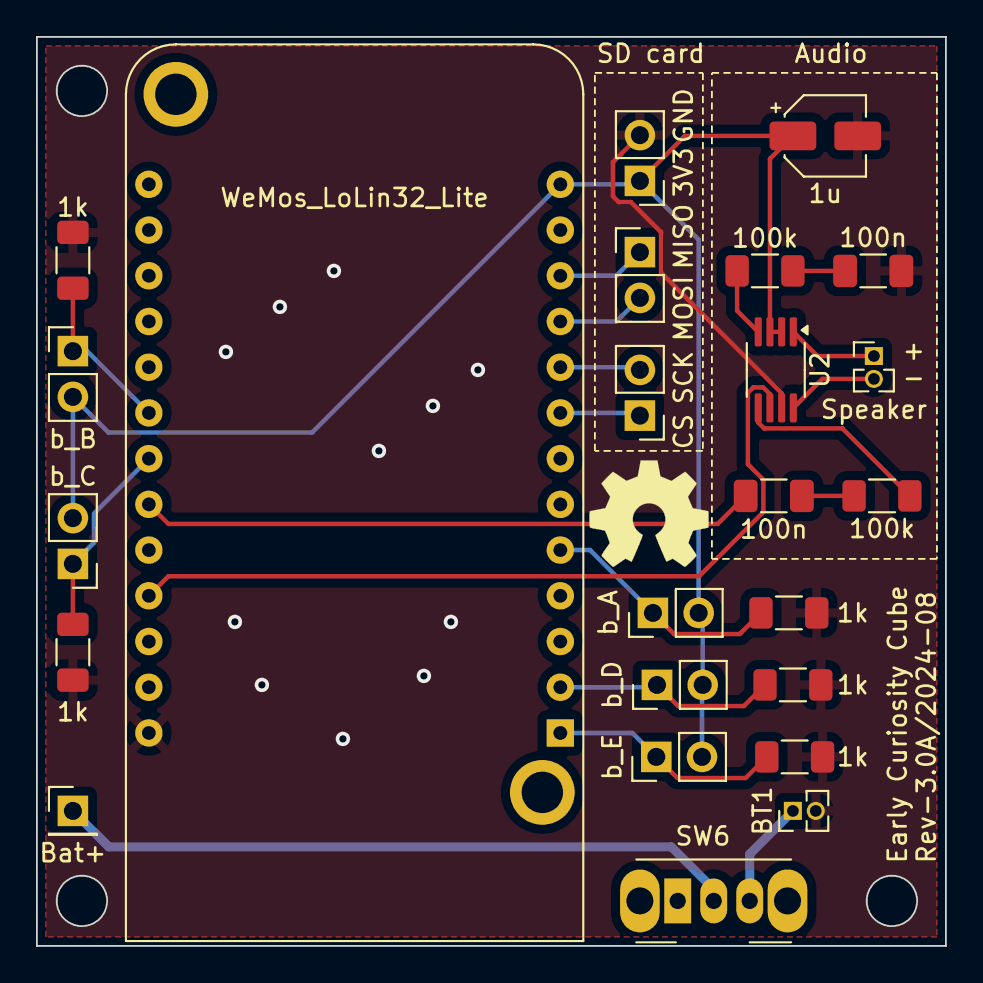
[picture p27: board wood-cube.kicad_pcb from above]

Board: 2 copper layers, 50.5 x 50.5 mm, 24 parts (0 on the bottom side), 21 nets.

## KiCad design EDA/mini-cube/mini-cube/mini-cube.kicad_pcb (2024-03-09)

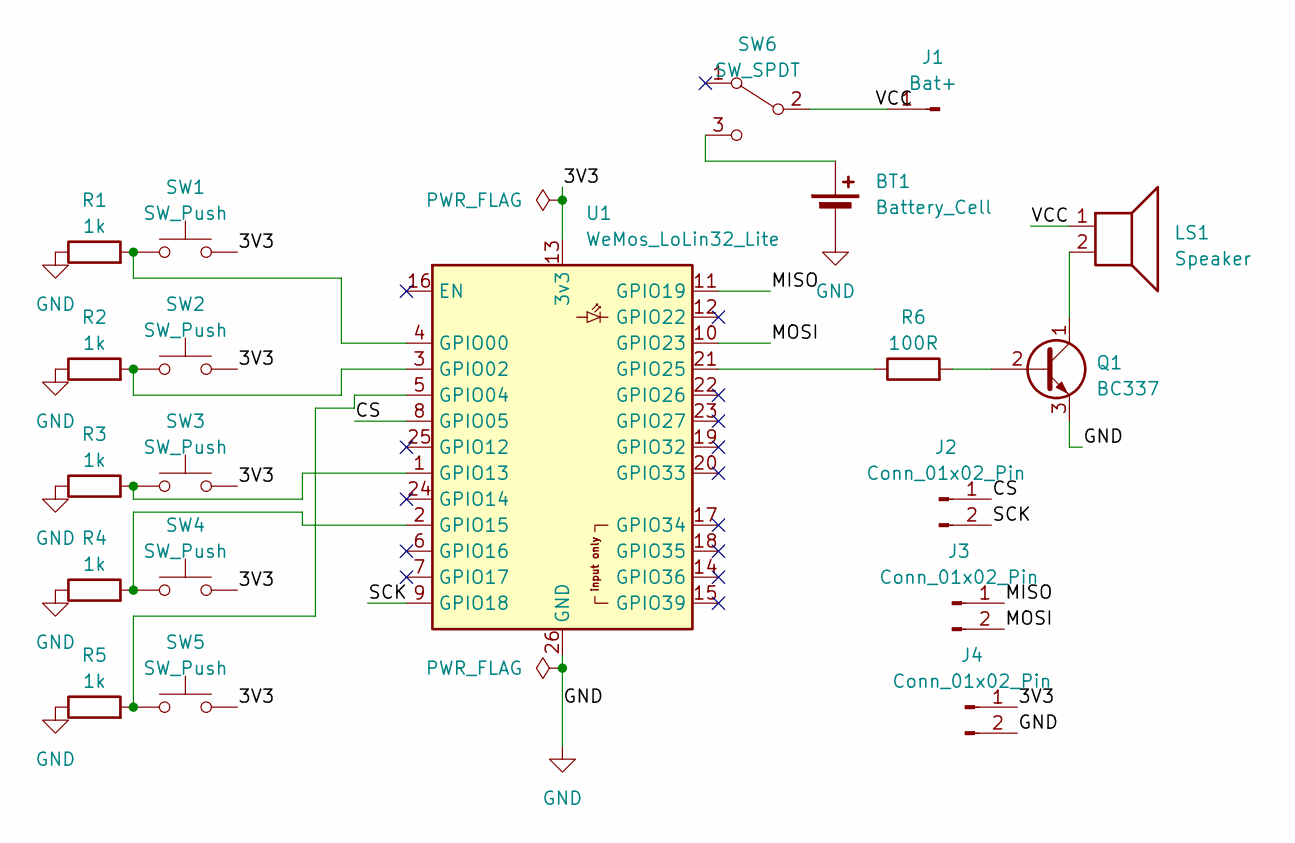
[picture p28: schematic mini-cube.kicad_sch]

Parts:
BT1: Battery_Cell; PinHeader_1x02_P1.27mm_Vertical
J1: Bat+; Pin_D1.0mm_L10.0mm
J2, J3, J4: Conn_01x02_Pin; PinHeader_1x02_P1.27mm_Vertical
LS1: Speaker; PinHeader_1x02_P1.27mm_Vertical
Q1: BC337; TO-92_Inline_Wide
R1, R2, R3, R4, R5: 1k; R_Axial_DIN0207_L6.3mm_D2.5mm_P2.54mm_Vertical
R6: 100R; R_Axial_DIN0207_L6.3mm_D2.5mm_P2.54mm_Vertical
SW1, SW2, SW3, SW4, SW5: SW_Push; PinHeader_1x02_P1.27mm_Vertical
SW6: SW_SPDT; SW_Slide_1P2T_CK_OS102011MS2Q
U1: WeMos_LoLin32_Lite; WEMOS_LoLin32_Lite

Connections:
/3V3: J4.1, SW1.2, SW2.2, SW3.2, SW4.2, SW5.2, U1.13 (3v3)
/CS: J2.1, U1.8 (GPIO05)
/MISO: J3.1, U1.11 (GPIO19)
/MOSI: J3.2, U1.10 (GPIO23)
/SCK: J2.2, U1.9 (GPIO18)
/VCC: J1.1, LS1.1, SW6.2 (B)
GND: J4.2, Q1.3 (E), R1.1, R2.1, R3.1, R4.1, R5.1, U1.26 (GND); also elsewhere on the board
unnamed 7: BT1.1 (+), SW6.3 (C); also elsewhere on the board
unnamed: Q1.2 (B), R6.2
unnamed: LS1.2, Q1.1 (C)
unnamed: R1.2, SW1.1, U1.4 (GPIO00)
unnamed: R2.2, SW2.1, U1.3 (GPIO02)
unnamed: R5.2, SW5.1, U1.5 (GPIO04)
unnamed: R3.2, SW3.1, U1.1 (GPIO13)
unnamed: R4.2, SW4.1, U1.2 (GPIO15)
unnamed: R6.1, U1.21 (GPIO25)

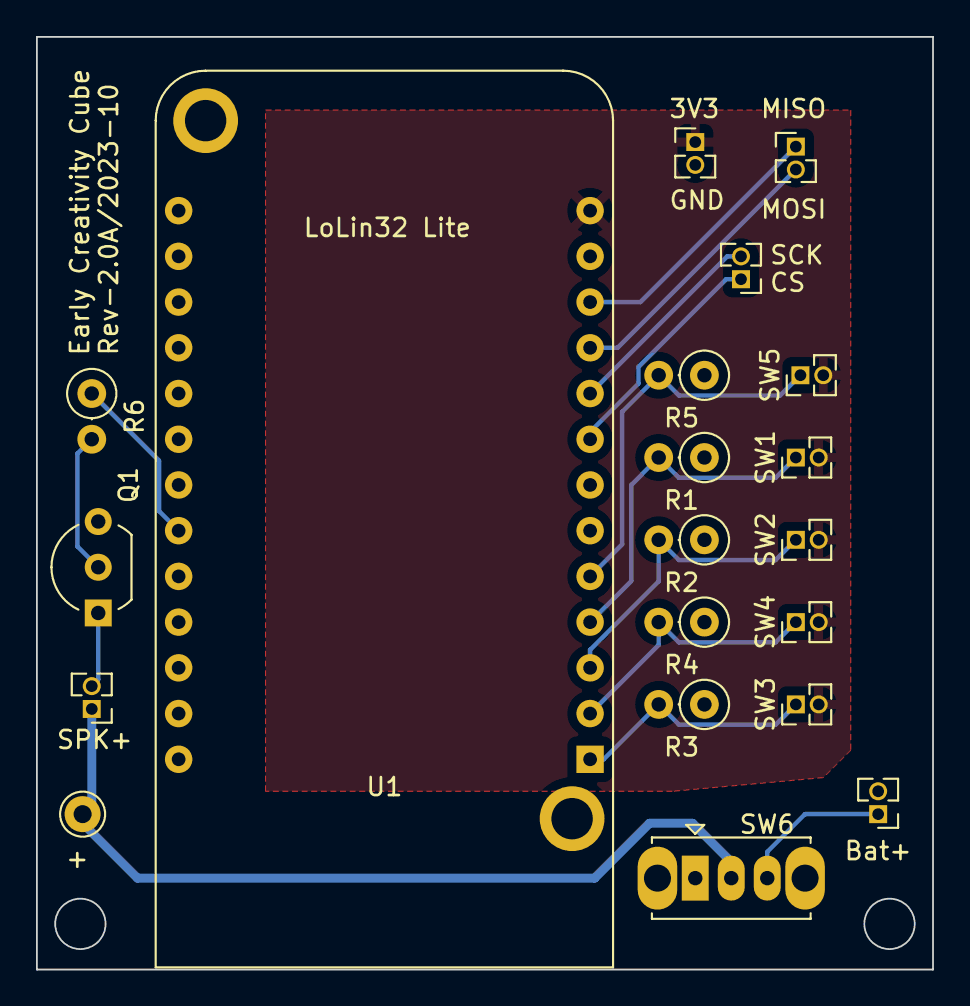
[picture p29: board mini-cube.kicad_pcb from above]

Board: 2 copper layers, 49.8 x 51.8 mm, 20 parts (0 on the bottom side), 16 nets.

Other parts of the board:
Bat+: Battery_Cell; PinHeader_1x02_P1.27mm_Vertical

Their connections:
GND: Bat+.2 (-); also elsewhere on the board
unnamed 7: Bat+.1 (+); also elsewhere on the board

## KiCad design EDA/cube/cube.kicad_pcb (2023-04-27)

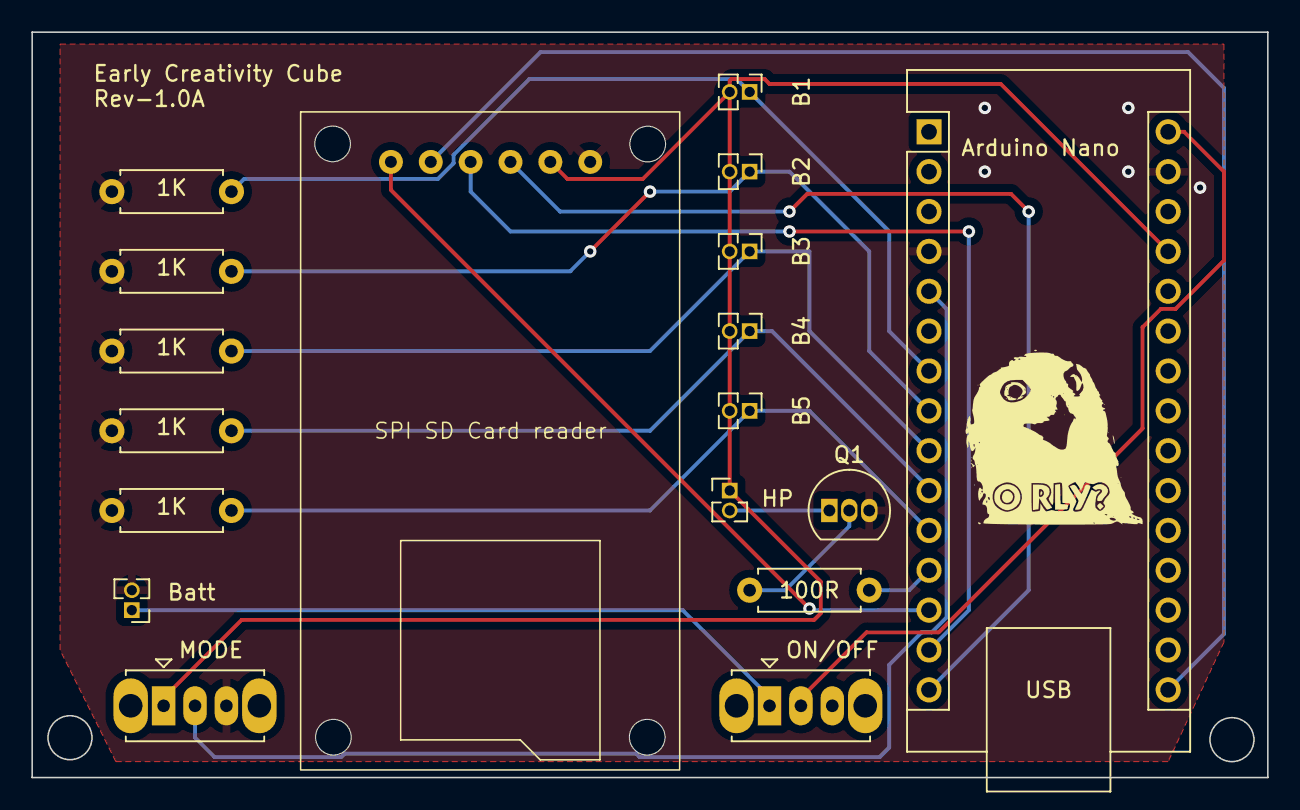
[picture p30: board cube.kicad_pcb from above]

Board: 2 copper layers, 78.7 x 47.5 mm, 18 parts (0 on the bottom side), 17 nets.

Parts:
1K, 1K#2, 1K#3, 1K#4, 1K#5: 1k; R_Axial_DIN0207_L6.3mm_D2.5mm_P7.62mm_Horizontal
100R: 100R; R_Axial_DIN0207_L6.3mm_D2.5mm_P7.62mm_Horizontal
Arduino Nano: Arduino_Nano_Every; Arduino_Nano
B1, B2, B3, B4, B5: SW_Push; PinHeader_1x02_P1.27mm_Vertical
Batt: Battery_Cell; PinHeader_1x02_P1.27mm_Vertical
HP: Speaker; PinHeader_1x02_P1.27mm_Vertical
MODE: SW_SPDT; SW_Slide_1P2T_CK_OS102011MS2Q
ON/OFF: SW_SPDT; SW_Slide_1P2T_CK_OS102011MS2Q
Q1: BC337; TO-92_Inline
SPI SD Card reader: SD_AZDelivery

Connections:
/VCC: Arduino Nano.27 (+5V), B1.2, B2.2, B3.2, B4.2, B5.2, HP.1, MODE.1 (A), SPI SD Card reader.2 (VCC)
/Vin: Arduino Nano.30 (VIN), ON/OFF.2 (B)
GND: 1K.1, 1K#2.1, 1K#3.1, 1K#4.1, 1K#5.1, Arduino Nano.4 (GND), Arduino Nano.29 (GND), Batt.2 (-), MODE.3 (C), Q1.3 (E), SPI SD Card reader.1 (GND)
unnamed: Arduino Nano.5 (D2), MODE.2 (B)
unnamed: 1K#5.2, Arduino Nano.7 (D4), B1.1
unnamed: 1K.2, Arduino Nano.8 (D5), B2.1
unnamed: 1K#2.2, Arduino Nano.9 (D6), B3.1
unnamed: 1K#4.2, Arduino Nano.10 (D7), B4.1
unnamed: 1K#3.2, Arduino Nano.11 (D8), B5.1
unnamed: 100R.1, Arduino Nano.12 (D9)
unnamed: Arduino Nano.13 (D10), SPI SD Card reader.6 (CS)
unnamed: Arduino Nano.15 (MISO), SPI SD Card reader.3 (MISO)
unnamed: Arduino Nano.14 (MOSI), SPI SD Card reader.4 (MOSI)
unnamed: Arduino Nano.16 (SCK), SPI SD Card reader.5 (SCK)
unnamed: Batt.1 (+), ON/OFF.1 (A)
unnamed: 100R.2, Q1.2 (B)
unnamed: HP.2, Q1.1 (C)

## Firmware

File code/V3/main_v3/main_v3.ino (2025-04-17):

/**
 * WARNING Stay on esp32 library version <3.0.0. Version 2.0.17 is working fine.
 * With later version, they complied with ESP32 IDF v5, which changes lots of
 * definitions and breaks the compatibility of the audio library using the
 * internal DAC.
 * ESP 32 is a serie of microcontroler. 
 */

 /** All this code was in C ++
 This type of code is based on the following nomenclature
 
 Type of function, function name (paremeter1, parameter2, ...,) { Bloc of several instructions}
 Four type of principal functions
 Void function () {} // void mute function
 int function () {} // integer function, the expected output of this function is specificaly an integer.
 bool function () {} // boolean function, the expected output of this function is specificaly a bolean TRUE vs FALSE. 
 float function () {} // float function, the expectd output of this function is specificaly a float. 
*/

#include "Arduino.h" // the function "#include" is to load the library, is the equivalent of import in python and library in R. 
#include "Audio.h"
#include "FS.h"
#include <driver/i2s.h>

#define SD_CS          5 // the number five indicate that it is the fith pin. Thus here the SD card is connected to the fifth part.
#define SPI_MOSI      23
#define SPI_MISO      19
#define SPI_SCK       18
#define button_A       4 // Top face
#define button_B      32 // Board side
#define button_C      33 // Speaker side
#define button_D      15 // Left side
#define button_E      13 // Right side

#define PAM8304_SD    27 // /SD input of the audio amplifier

#define led_pin 22

// In this project, we designed 5 cubes with different configurations based on the following modes:

/*
 MODE_ALPHA: Always plays sound. This mode corresponds to the code section where #define MODE_ALPHA is used.
 */

/*
 * MODE_BETA: No sound. This mode corresponds to the code section where #define MODE_BETA is used.
 */

/*
 * MODE_GAMMA: Alternates between playing sound and no sound. This mode corresponds to the code section where #define MODE_GAMMA is used.
 */

/*
 * MODE_DELTA (YesNoYes): No sound for the first 7 interactions, then plays sound on the 8th interaction. This mode corresponds to the code section where #define MODE_DELTA is used.
 */

#define MODE_ALPHA


/**
 * Global variables
 */
int i; // Declares an integer variable named "i". This can be used for counting or indexing. In this case the purpose it to count the number of index for itterations 
unsigned long curtime;
// Declares a variable "curtime" to store the current time in milliseconds. This code is done to timing the operation, in this case, it permit to calculate the time duration of each button pression.
// This is useful for measuring how long something takes or timing events.

File myFile;
// Declares a variable "myFile" to work with files on an SD card.
// This allows the program to read from or write to files.

// The filename for experiment files is built in three parts:
const char* exp_ID_filename = "/exp_ID.txt";
// The base part of the filename, common to all experiment files. For some reason, the leading '/' is now required. In this case the line said to some extend "store the experiment ID counter"
const char* exp_filename_base = "/exp_";
// A file that stores the unique ID for each experiment, ensuring each filename is different. It is to some extend the "prefix" for each experiment file
const char* exp_filename_extension = ".csv";
// The file extension, indicating the file format (CSV in this case).

String exp_filename;
// A variable to hold the complete filename for the current experiment file.
// This is built using the base name, experiment ID, and file extension.

char buf[4];
// A small storage space (array) to temporarily hold data read from files, like the experiment ID.

int exp_ID = 0;
// A variable to store the current experiment ID, read from a file and incremented for each new experiment.

int modeSwitchTime = 4000;
// A variable to store a time duration in milliseconds (e.g., 4000 milliseconds = 4 seconds).
// The following sections define headers for logging data in different modes:


#ifdef  MODE_ALPHA 
// if the code detect that we use the cube alpha thus, it consider the sequence as follow.
const char* measures_header = "observation, face, pression_start, pression_stop, sound, isExperiment, alpha";
#endif
// Defines the columns for logging data in MODE_ALPHA.

#ifdef  MODE_BETA
const char* measures_header = "observation, face, pression_start, pression_stop, sound, isExperiment, beta";
#endif
#ifdef  MODE_GAMMA
const char* measures_header = "observation, face, pression_start, pression_stop, sound, isExperiment, gamma";
#endif
#ifdef  MODE_DELTA
const char* measures_header = "observation, face, pression_start, pression_stop, sound, isExperiment, delta";
#endif

bool triggered[5] = {false, false, false, false, false};
// An array to track whether each of the 5 buttons has been pressed.
// Initialized to "false" to indicate no buttons have been pressed at the start.

bool rising_edge[5] = {false, false, false, false, false};
bool rising_edge_detected[5] = {false, false, false, false, false};
// Arrays to track the start (rising edge) and end (falling edge) of button presses.

bool falling_edge[5] = {false, false, false, false, false};
unsigned long rising_time[5] = {0, 0, 0, 0, 0};
// An array to store the time when each button was first pressed.
// Initialized to 0, indicating no buttons have been pressed yet.

unsigned int cur_obs = 1;
// A variable to track the current observation number, starting at 1.

unsigned int demo_press_count = 0;
// A variable to count the number of demo button presses, starting at 0.

bool isStandby = false; // True, do not do anything in the main loop.
bool isExperiment = false; // False is demo, true is experiment
bool experimentEntry = false; // A variable to track entry into the experiment mode.

Audio audio(true, I2S_DAC_CHANNEL_BOTH_EN); // Initializes an audio object for playing sound using both audio channels.

bool eof = false; // A variable to track if the end of the audio file has been reached.

void(* resetFunc) (void) = 0;
// Declares a function pointer that can be used to reset the system.
// Initialized to 0, meaning it doesn't point to any function initially.

void audio_eof_mp3(const char *info){  //end of file
    eof = true;
}
// A function called when the end of the audio file is reached, setting "eof" to true.
//eof means "end of file", thus the idea here is to say, when the audio last part of the sound is finished flag it as finished

/*
 * Function: play_audio
 * -------------------
 * Plays the current audio file to completion and prepares the next one.
 * 
 * The function works by:
 * 1. Running audio.loop() continuously until the end of file is reached
 * 2. Resetting the EOF flag after playback completes
 * 3. Loading the next audio file (sound.mp3) from SD card
 * 
 * Note: This function only loads the next file but does not start playing it.
 * Another call to play_audio() or other playback trigger would be needed to
 * play the newly loaded file.
 */


void play_audio() {
  // Continue processing audio data until end of file is reached
  while(not eof) {
    audio.loop();
  }
  // Reset EOF flag after playback completes
  eof = false;
  //audio.connecttoFS(SD, "/bird.mp3");  // Previously used audio file (disabled)
  audio.connecttoFS(SD, "/sound.mp3"); // Load next audio file from SD card
}


/** **********************
 *  
 *  SETUP
 * 
 * ***********************
 */
void setup() {
  // The setup function runs once when Arduino starts up
  // It initializes all necessary components and settings before the main program loop begins
  
  delay(100);
  // Short delay to ensure hardware is stable after power-up
  // Gives components time to reach proper operating state
  
  // while(!Serial);  
  // Commented out code - would wait until Serial connection is established
  // Useful for debugging when you need to see all messages from the beginning

  Serial.begin(115200);
  // Starts serial communication between Arduino and computer at 115200 bits per second
  // IMPORTANT: Set your Serial Monitor to the same baud rate (115200) or you will not see output

  /* Do not know why the delay works, but it avoids running the setup twice, creating empty experiments. */
  delay(1000);
  // One second delay prevents an issue where setup might run twice
  // This helps ensure reliable experiment initiation and prevents empty data records

  Serial.println("Starting setup");
  // Sends a message to Serial Monitor indicating setup has begun
  // Useful for confirming the program is running and tracking execution flow

 
  // === SD CARD INITIALIZATION ===
  
  pinMode(SD_CS, OUTPUT);
  // Configures the SD card's Chip Select pin as an OUTPUT
  // SD_CS is a pin number defined in line 25 in the code and correspond to the pin 5. 
  // This pin controls when the Arduino communicates with the SD card

  digitalWrite(SD_CS, HIGH);
  // Sets the SD card's Chip Select pin to HIGH (inactive state)
  // This temporarily disables communication with the SD card
  // When HIGH, the SD card ignores commands on the SPI bus

  SPI.begin(SPI_SCK, SPI_MISO, SPI_MOSI);
  // Initializes the SPI communication protocol with specified pins:
  // - SCK: Clock signal that synchronizes data transmission
  // - MISO: Master In Slave Out - data from SD card to Arduino
  // - MOSI: Master Out Slave In - data from Arduino to SD card
  // SPI is the protocol used to communicate with SD cards and many other devices

  SPI.setFrequency(1000000);
  // Sets SPI communication speed to 1 MHz (1,000,000 Hz)
  // Lower frequencies provide more reliable communication with SD cards
  // Higher frequencies may cause errors with some SD cards or longer wires
  
  // IMPORTANT: This 1MHz frequency only sets the communication speed between the Arduino and SD card hardware.
  // It does NOT determine the sampling rate or how many data points per second will be saved in your CSV file.
  // Your actual data collection frequency is determined by your main program's timing code.
  
  if(!SD.begin(SD_CS)){
  // Attempts to initialize the SD card using the Chip Select pin
  // If initialization fails (returns false), the code inside these brackets runs
    
    Serial.println("Card Mount Failed, reset.");
    // Sends error message to Serial Monitor
    // "Card Mount Failed" means the Arduino couldn't establish communication with the SD card
    
    resetFunc();
    // Calls a function (defined elsewhere) that restarts the Arduino
    // This is a recovery mechanism - if SD card fails, start over
    
    return;
    // Exits the setup function early
    // Program won't continue beyond this point if SD card initialization failed
  }



// === BUTTON SETUP ===

  pinMode(button_A, INPUT);
  pinMode(button_B, INPUT);
  pinMode(button_C, INPUT);
  pinMode(button_D, INPUT);
  pinMode(button_E, INPUT);
  
  // Configures pins for buttons A through E as INPUTS
  // This tells the Arduino to read voltage levels on these pins
  // When buttons are pressed, the Arduino will detect the voltage change
  // Note: You might need pull-up/pull-down resistors depending on your button circuit


// === AUDIO AMPLIFIER SETUP ===

  pinMode(PAM8304_SD, OUTPUT);
  // Sets the PAM8304_SD pin as an OUTPUT
  // This pin controls the PAM8304 audio amplifier's shutdown mode.
  
  
  digitalWrite(PAM8304_SD, HIGH);
  // Sets the PAM8304_SD pin HIGH which activates the amplifier
  // LOW would put the amplifier in shutdown/sleep mode to save power
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

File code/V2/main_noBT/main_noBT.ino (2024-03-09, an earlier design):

#include "Arduino.h"
#include "Audio.h"
#include "BluetoothSerial.h" //Header File for Serial Bluetooth, will be added by default into Arduino
#include "FS.h"

#define SD_CS          5
#define SPI_MOSI      23
#define SPI_MISO      19
#define SPI_SCK       18
#define button_A       4 // Top face
#define button_B      32 // Board side
#define button_C      33 // Speaker side
#define button_D      15 // Left side
#define button_E      13 // Right side

#define led_pin 22

/* Alpha: Always play sound */
#define MODE_ALPHA
/* Beta: No sound */
//#define MODE_BETA
/* Gamma: Sound / No sound */
//#define MODE_GAMMA
/* Delta (YesNoYes): No sound / No sound / Sound */
//#define MODE_DELTA

/**
 * Global variables
 */
int i;
unsigned long curtime;
File myFile;
const char* exp_ID_filename = "/exp_ID.txt"; // For some reason, the leading '/' is now required.
const char* exp_filename_base = "/exp_";
const char* exp_filename_extension = ".csv";
String exp_filename;
char buf[4];
int exp_ID = 0;

int modeSwitchTime = 2000; // 2 seconds
  
#ifdef  MODE_ALPHA
const char* measures_header = "observation, face, pression_start, pression_stop, sound, isExperiment, alpha";
#endif
#ifdef  MODE_BETA
const char* measures_header = "observation, face, pression_start, pression_stop, sound, isExperiment, beta";
#endif
#ifdef  MODE_GAMMA
const char* measures_header = "observation, face, pression_start, pression_stop, sound, isExperiment, gamma";
#endif
#ifdef  MODE_DELTA
const char* measures_header = "observation, face, pression_start, pression_stop, sound, isExperiment, delta";
#endif

bool triggered[5] = {false, false, false, false, false};
bool rising_edge[5] = {false, false, false, false, false};
bool falling_edge[5] = {false, false, false, false, false};
unsigned long rising_time[5] = {0, 0, 0, 0, 0};
unsigned int cur_obs = 1;
unsigned int demo_press_count = 0;

bool isStandby = false; // True, don't do anything in the main loop.
bool isExperiment = false; // False is demo, true is experiment
bool experimentEntry = false;

BluetoothSerial BtSerial; // Object for Bluetooth

Audio audio(true, I2S_DAC_CHANNEL_BOTH_EN);

bool eof = false;

void(* resetFunc) (void) = 0;

void audio_eof_mp3(const char *info){  //end of file
    eof = true;
}

void play_audio() {
  while(not eof) {
    audio.loop();
  }
  eof = false;
  //audio.connecttoFS(SD, "/bird.mp3");
  audio.connecttoFS(SD, "/sound.mp3");
}
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

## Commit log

2023-04-12 [EDA] Schematic
    [cube.kicad_sch]
2023-04-12 [CAD] Cube FreeCAD file.
    [cube_v2.FCStd]
2023-04-12 [Code] Working prototype.
    - Checks the experiment number in a file.
    - Saves the measurements in a file.
    TODO:
    - Sound
    - Modes
2023-04-27 [EDA] PCB v1.0-revA
    [cube.kicad_pcb, cube.kicad_sch]
2023-04-27 [CAD] Cube v2 and STL
    [cube_v2.1-Bottom.stl, cube_v2.1-trap.stl, cube_v2.FCStd, cube_v2.stl]
2023-04-28 [Doc] How to update the Arduino
2024-03-09 [V2] EDA
    [mini-cube.kicad_pcb, mini-cube.kicad_sch]
2024-03-09 [V2] Code and CAD
    [cube_v3.1-Body.stl, cube_v3.1-Bot_plain.stl, cube_v3.1-Bottom.stl, cube_v3.1-trap.stl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]
2024-10-20 [v3] EDA files for wood cube.
    [wood-cube.kicad_pcb, wood-cube.kicad_sch]
2024-10-20 [v3] CAD files for laser cutting v3.
    [cube_v4-Shape2DView.dxf, cube_v4-Shape2D_bottom.dxf, cube_v4-Shape2D_magnet_plate.dxf, cube_v4-Shape2D_pcb_plate.dxf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]
2025-04-17 Update main_v3.ino
    Update of main_v3 with annotations – Romain di Stasi, version dated April 17th, 2025.
